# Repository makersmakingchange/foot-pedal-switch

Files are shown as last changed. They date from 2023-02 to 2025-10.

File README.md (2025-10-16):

# Foot Pedal Switch
The Foot Pedal Switch is an assistive switch with a standard 3.5 mm mono jack that can be operated with a foot.

This design is by John Park and was posted as part of an Adafruit Learning guide (https://learn.adafruit.com/diy-adaptive-game-controllers/interfacing-buttons-and-switches#foot-pedal-3015364-27).

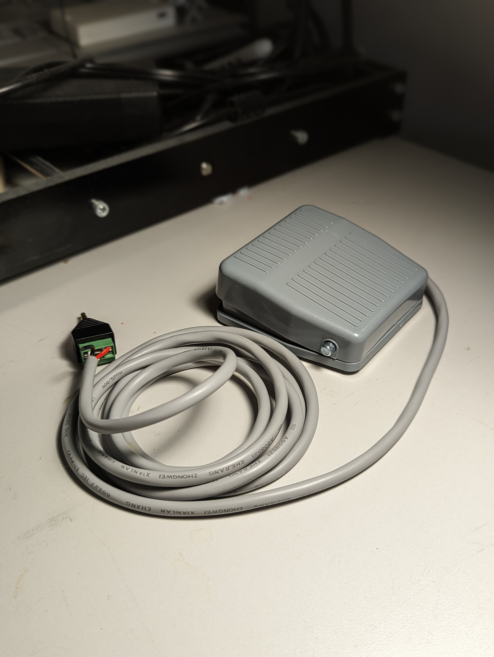
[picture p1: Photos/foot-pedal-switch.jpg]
A grey Foot Pedal Switch with an attached 3.5 mm cable sitting on a table.


## More info at
- [Makers Making Change Project Page](https://www.makersmakingchange.com/product/foot-pedal-switch/01tJR0000009Sl3YAE)

Foot Pedal Switch
### 1. Do it Yourself (DIY) or Do it Together (DIT)

This is an open-source assistive technology, so anyone is free to build it. All of the files and instructions required to build the Foot Pedal Switch are contained within this repository. Refer to the Maker Checklist below.

### 2. Request a build of this device

If you would like to obtain a Foot Pedal Switch, you may submit a build request through the [MMC Library Page](https://makersmakingchange.com/project/foot-pedal-switch/). The requestor is responsible for the cost of materials and any shipping.

### 3. How to build this device for someone else

If you have the skills and equipment to build this device, and would like to donate your time to create the switch for someone who needs it, visit the [MMC Maker Wanted](https://makersmakingchange.com/maker-wanted/) section.

## Getting Started

### 1. Read the Makers Checklist

The Makers Checklist contains a list of steps outling the process to create the device.

### 2. Order the Off-The-Shelf Components

The [Bill of Materials](/Documentation/Foot_Pedal_Switch_BOM.xlsx) lists all of the parts and components required to build the Foot Pedal Switch. The all components needs to be ordered online. 

### 3. Assemble the Foot Pedal Switch

Reference the [Assembly Guide](/Documentation/Foot_Pedal_Switch_Assembly_Guide.pdf) for the tools and steps required to build each portion.

## Files
### Documentation
| Document             | Version | Link |
|----------------------|---------|------|
| Design Rationale     | 1.2     | [Foot_Pedal_Switch_Design_Rationale](/Documentation/Foot_Pedal_Switch_Design_Rationale.pdf)     |
| Maker Checklist      | 1.2     | [Foot_Pedal_Switch_Maker_Checklist](/Documentation/Foot_Pedal_Switch_Maker_Checklist.pdf)     |
| Bill of Materials    | 1.2     | [Foot_Pedal_Switch_Bill_of_Materials](/Documentation/Foot_Pedal_Switch_BOM.xlsx)     |
| Assembly Guide       | 1.2     | [Foot_Pedal_Switch_Assembly_Guide](/Documentation/Foot_Pedal_Switch_Assembly_Guide.pdf)     |
| 3D Printing Guide    | 1.2     | [Foot_Pedal_Switch_3D_Printing_Guide](/Documentation/Foot_Pedal_Switch_3D_Printing_Guide.pdf)     |
| User Guide           | 1.2     | [Foot_Pedal_Switch_User_Guide](/Documentation/Foot_Pedal_Switch_User_Guide.pdf)    |
| Changelog            | 1.2     | [Foot_Pedal_Switch_Changelog](/Documentation/Foot_Pedal_Switch_Changelog.pdf)     |

### Design Files
 - [CAD Files](/Design_Files)

### Build Files
 - [3D Printing Files](/Build_Files/3D_Printing_Files)

## Attribution
 - Design by [John Park](https://learn.adafruit.com/diy-adaptive-game-controllers/interfacing-buttons-and-switches#foot-pedal-3015364-27)
 - Documentation by Neil Squire Society/Makers Making Change

## License
Everything needed or used to design, make, test, or prepare the Foot Pedal Switch is licensed under the [Creative Commons Attribution-NonCommercial-ShareAlike 4.0 ](https://creativecommons.org/licenses/by-nc-sa/4.0/).

Accompanying material such as instruction manuals, videos, and other copyrightable works that are useful but not necessary to design, make, test, or prepare the Foot Pedal Switch are published under a Creative Commons Attribution-ShareAlike 4.0 license https://creativecommons.org/licenses/by-sa/4.0/ (CC BY-SA 4.0).

---
<!-- ABOUT MMC START -->
## About Makers Making Change
[Makers Making Change Logo](https://www.makersmakingchange.com/)

Makers Making Change is a program of [Neil Squire](https://www.neilsquire.ca/), a Canadian non-profit that uses technology, knowledge, and passion to empower people with disabilities.

Makers Making Change leverages the capacity of community based Makers, Disability Professionals and Volunteers to develop and deliver affordable Open Source Assistive Technologies.

 - Website: [www.MakersMakingChange.com](https://www.makersmakingchange.com/)
 - GitHub: [makersmakingchange](https://github.com/makersmakingchange)
 - Bluesky: [@makersmakingchange.bsky.social](https://bsky.app/profile/makersmakingchange.bsky.social)
 - Instagram: [@makersmakingchange](https://www.instagram.com/makersmakingchange)
 - Facebook: [makersmakechange](https://www.facebook.com/makersmakechange)
 - LinkedIn: [Neil Squire Society](https://www.linkedin.com/company/neil-squire-society/)
 - Thingiverse: [makersmakingchange](https://www.thingiverse.com/makersmakingchange/about)
 - Printables: [MakersMakingChange](https://www.printables.com/@MakersMakingChange)

### Contact Us
For technical questions, to get involved, or to share your experience we encourage you to [visit our website](https://www.makersmakingchange.com/) or [contact us](https://www.makersmakingchange.com/s/contact).
<!-- ABOUT MMC END -->

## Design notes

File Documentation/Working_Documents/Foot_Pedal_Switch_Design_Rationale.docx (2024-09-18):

# Introduction

This device is a foot pedal switch that functions like a standard 3.5mm mono jack switch, but can be operated with a foot.

# Research

Name | Picture | Price | Link

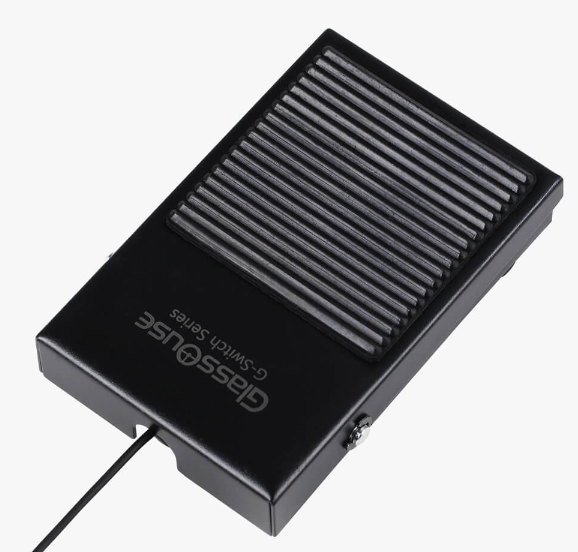
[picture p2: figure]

G-Switch GS04 | | $29.00 | Link (https://glassouse.com/product/foot-switch-glassouse-assistive-device-accessory-hands-free/)

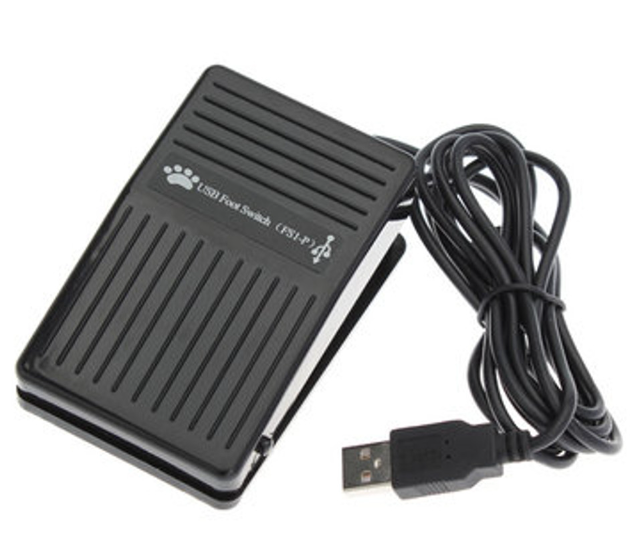
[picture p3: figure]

Single Foot Switch Computer Interface | | $41.60 | Link (https://www.adaptivetechsolutions.com/pd-single-foot-switch-computer-interface/)

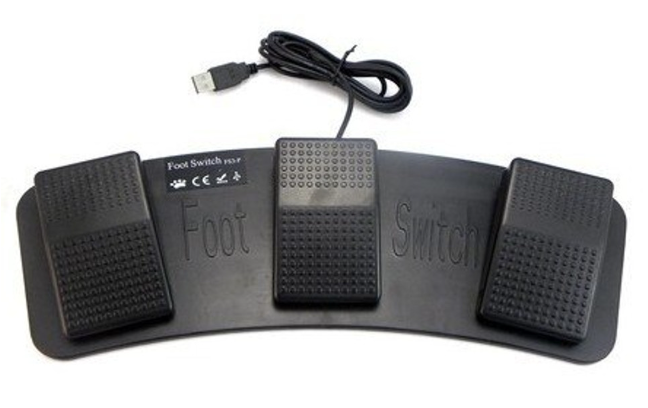
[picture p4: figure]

Three Switch Computer Controller Pedals | | $58.13 | Link (https://www.adaptivetechsolutions.com/pd-three-switch-computer-controller-foot-pedals/)

# Requirements

## Goals

G01 | Create a foot operated switch

## Functional Requirements

F01 | Activate a mono jack switch with activation of a foot pedal

## Non-functional Requirement

NF01 | Cost less than 15 dollars

## Constraints

C01 | Buildable by users with minimal experience soldering
C02 | Built using easily available components

# Testing

When the foot pedal switch was assembled, it was tested with the switch tested. It was found to have roughly a 1.5-pound activation weight and worked normally.

# Opportunities for Improvement

An enclosure could be designed to protect the wire connection between the switch and the jack.

# Metal Switch Body

It was found that for some use cases, the plastic switch body used in the original switch could shatter with heavy use, and some users wanted the cable to come out the same side as the hinge. A metal switch body was sourced on Amazon and added to the BoM and Maker Guide as an alternate design.

© 2023 by Neil Squire. This work is licensed under the CC BY SA 4.0 License: http://creativecommons.org/licenses/by-sa/4.0 Files available at https://makersmakingchange.com/project/foot-pedal-switch/ Page 1 of 1

V1.0 | February 2023 Foot Pedal Switch Design Rationale

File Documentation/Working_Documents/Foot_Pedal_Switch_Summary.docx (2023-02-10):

# Title

Foot Pedal Switch

## Subtitle

An assistive switch with a standard 3.5mm mono jack switch that is operated with a foot.

## Device Details

### Overview

This device is a foot pedal switch that functions like a standard 3.5 mm mono jack switch but can be operated with a foot.

### Usage

The switch is plugged into a 3.5 mm mono jack and can then be activated by pressing the pedal with your foot.

### Cost

~$15

### Build Instructions

This switch is assembled from commercially available components. The wires on the foot pedal switch are stripped and connected to the 3.5 mm mono jack terminal block.

#### Skills Required

- Screwdriver use
- Wire stripping

#### Time Required

- Assembly time: <5 min

#### Tools

- Wire stripper
- Screwdriver

#### Components

- 1X Foot pedal
- 1X 3.5 mm terminal jack

### Attribution

- Design by John Park (https://learn.adafruit.com/u/johnpark) on the Adafruit guide for interfacing buttons and switches (https://learn.adafruit.com/diy-adaptive-game-controllers/interfacing-buttons-and-switches)
- Documentation by Neil Squire Society/Makers Making Change

© 2023 by Neil Squire. This work is licensed under the CC BY SA 4.0 License: http://creativecommons.org/licenses/by-sa/4.0 Files available at https://makersmakingchange.com/project/foot-pedal-switch/ Page 1 of 1

V1.0 | February 2023 Foot Pedal Switch Summary

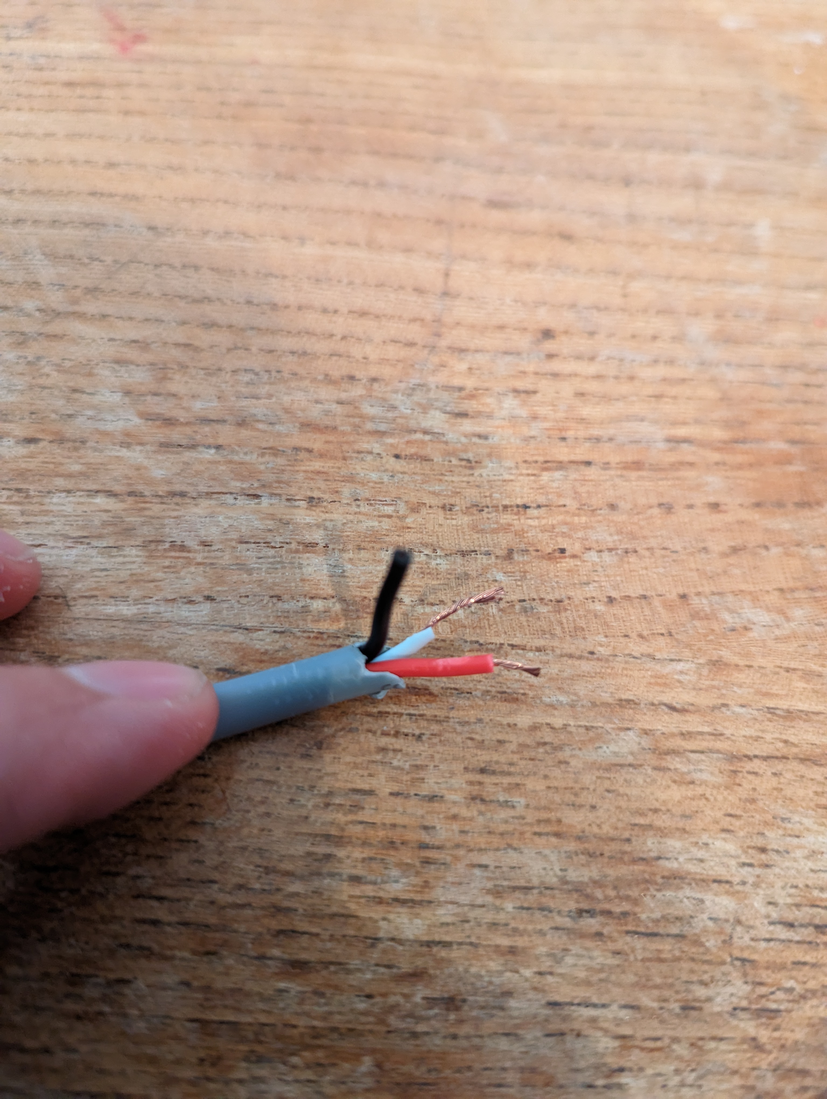
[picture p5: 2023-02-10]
Photos/Stripped wires.jpg

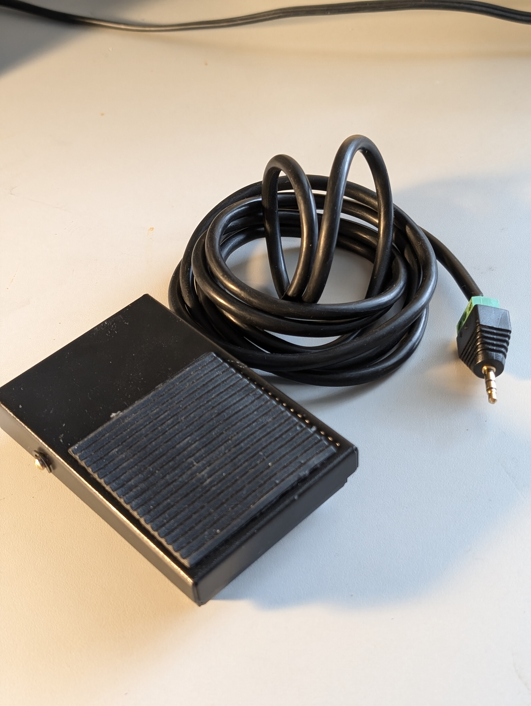
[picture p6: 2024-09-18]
Photos/Medal-Foot-Pedal-Switch.jpg

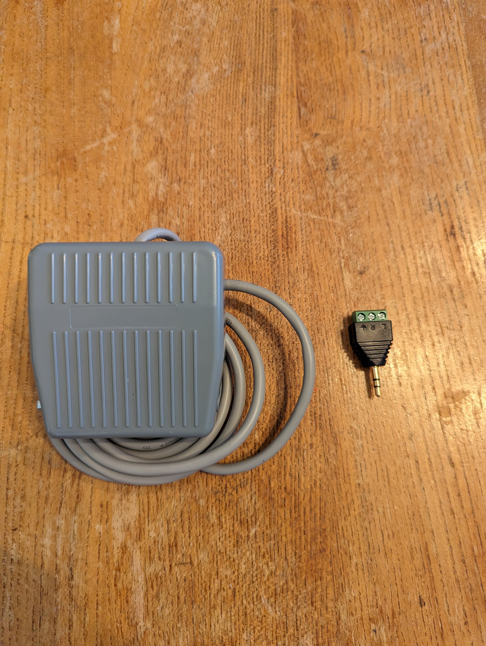
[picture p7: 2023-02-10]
Photos/Part Layout.jpg

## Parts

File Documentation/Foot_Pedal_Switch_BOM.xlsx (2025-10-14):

Foot Pedal Switch |  | Total Cost | Total Print time (hr) | Total filament (g)
Version: V1.2 | Last updated: 2024-Sept-16 | $14.84 | 1.73 | 17
Commercial Parts:
Part type (Electrical. Mechanical, Sanitization, ect) | Part Name | Quantity Needed | Pkg Quantity | Price per package | Price per Unit | Price for qty needed | Link
Electrical | Stereo Terminal Block | 1 | 1 | $3.60 | $3.60 | $3.60 | https://www.digikey.ca/en/products/detail/adafruit-industries-llc/2790/7241423
Electrical | Foot Switch | 1 | 1 | $10.81 | $10.81 | $10.81 | https://www.digikey.ca/en/products/detail/adafruit-industries-llc/423/5353597
3D Printed Parts ESTIMATED PRICING USING 1KG ROLL COST: | $25.00
Part | Description | Quantity Needed | TOTAL Mass (g) | Estimated Price | Print Time (Min) | Link
Bracket V2 | bracket to mount foot pedal to the ground | 1 | 17 | $0.43 | 104
 |  |  |  | $0.00
 |  |  |  | $0.00
 |  |  |  | $0.00
 |  |  |  | $0.00
 |  |  | Total Print Cost: | $0.43
Tools for Assembly
Wire stripper
Screwdriver
Alternatives (if there are other sources for some parts link them below)
Part and description | Link | Price
Metal Foot Pedal alternative (2-pack) | amazon.ca/gp/product/B09WN6MVVH | $23.85

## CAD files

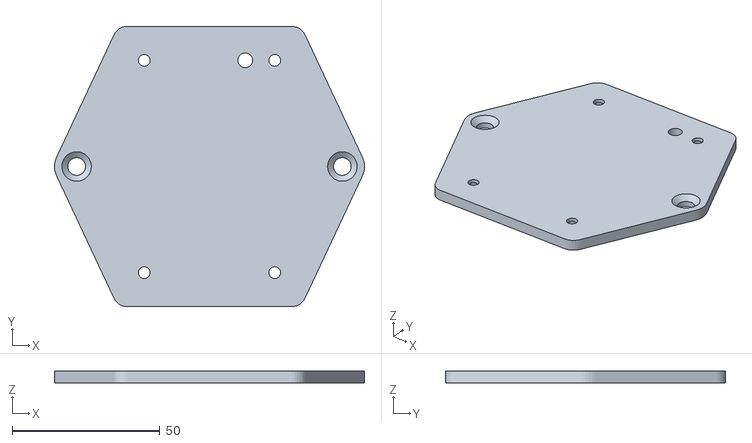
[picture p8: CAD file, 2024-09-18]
Build_Files/3D_Printing_Files/Metal Pedal Bracket.stl
105.0 x 95.0 x 4.00

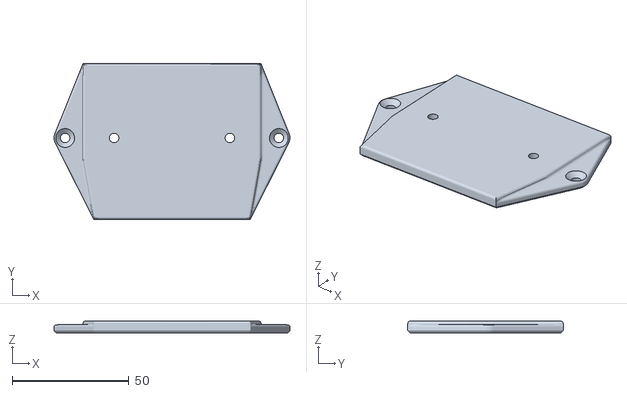
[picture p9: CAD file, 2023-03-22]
Build_Files/3D_Printing_Files/Plastic Pedal Bracket.stl
101.0 x 66.5 x 5.00

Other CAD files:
Design_Files/Metal Foot Pedal Bracket.f3d
Design_Files/Plastic Foot Pedal Bracket.f3d

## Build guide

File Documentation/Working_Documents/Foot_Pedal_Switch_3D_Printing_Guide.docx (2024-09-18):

# 3D Printing Summary

Metrics
Total Print Time (min) | 104
Total Number of Components | 2
Typical Total Mass (g) | 17
Typical Number of Print Setups | 1

# 3D Printing Settings

Print File Name | Qty | Total Print Time (hr:min) | Mass (g) | Infill (%) | Support(Y/N) | Layer Height/ Nozzle Diameter(mm) | Notes (orientation, special settings, etc.)
Plastic Pedal Bracket.stl | 1 | 1:54 | 17 | 20 | N | 0.2/0.4 | - Print in orientation given in STL
Metal Pedal Bracket.stl | 1 | 2:29 | 21 | 20 | N | 0.2/0.4 | - Print in orientation given in STL

# Customization Options

- The bracket can be printed in any colour the user would like

# Post-Processing

- Use a hobby knife or sandpaper to remove any sharp edges

© 2023 by Neil Squire. This work is licensed under the CC BY SA 4.0 License: http://creativecommons.org/licenses/by-sa/4.0 Files available at https://makersmakingchange.com/project/foot-pedal-switch/ Page 2 of 3

V1.1 | March 2023 Foot Pedal Switch 3D Printing Guide

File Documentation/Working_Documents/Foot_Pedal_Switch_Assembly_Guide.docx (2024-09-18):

# Required Components

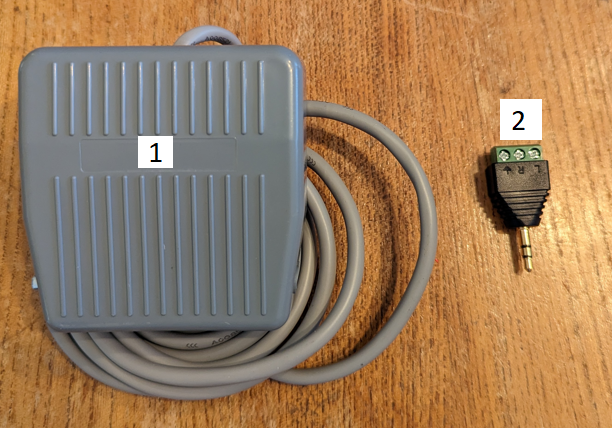
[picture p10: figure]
Both components of the foot pedal switch laid out and numbered

| BOM 1. Foot Pedal 2. Terminal Jack

# Optional Components

- Plastic Pedal Bracket
- Metal Pedal Bracket
- Metal Switch Body

# Required Tools

- Wire stripper
- Screwdriver

# Assembly Instructions

## Step 1

Strip 1 cm from the end of the pedal wire. Strip 1cm from the white and red wire as well; leave the black wire unstripped. If using the metal foot pedal, this step is the same, strip the white and red wires.

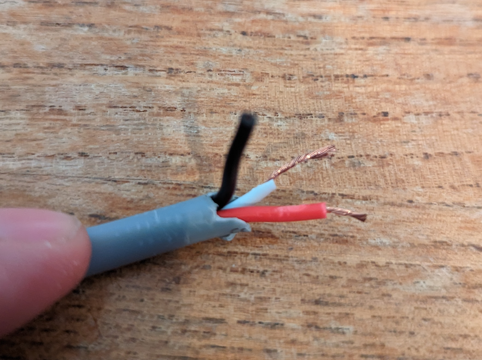
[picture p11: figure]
The grey wire casing on the pedal stripped back, with the red and white wires inside stripped as well.

## Step 2

Connect the white wire to the ground terminal on the jack, and the red wire to the L terminal on the jack. This creates a switch that is activated when the pedal is pressed. Connecting the black wire to the L terminal instead creates a switch that is always active and is deactivated when the switch is pressed. When using the metal foot pedal switch, the instructions are the same, with the white wire to the ground (right) terminal and red wire to the L (left) terminal.

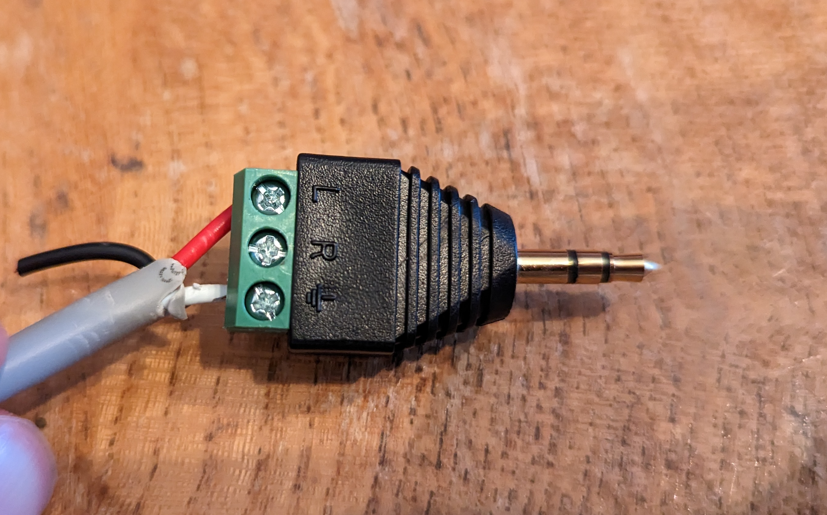
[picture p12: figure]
The terminal block attached to the red and white wires.

## Step 3 (Optional)

If using the plastic pedal bracket, remove the two screws and the four rubber feet on the bottom of the switch. The rubber feet can be removed by pulling, they are only held in place by an adhesive. Fit the bracket in place with the counterbored screw holes facing away from the switch, matching the orientation of the screws. Replace the two screws removed earlier, fastening the bracket in place. The bracket can now be screwed to a surface to hold the switch in place.

If using the metal pedal bracket, use a screwdriver to remove the feet of the pedal, and set aside the screws. Line up the bracket with the screw holes for the foot pedal and screw it into place using the screws from the feet. The bracket should only fit one way, since the screw sticking out the base only allows the bracket to fit when the hole on the bracket is aligned to the screw on the base. After the four base screws are secured, the bracket can now be screwed to a surface to hold the switch in place.

# Testing

Connect the 3.5mm jack to a switch tester or switch adapted toy and press the pedal.

## Constantly On

If the switch is constantly on, check that there are not any shorts between the wires, and that they are screwed into the correct terminal blocks in the jack. The normally open wire should be screwed into the L terminal, and the common wire should be connected to the ground terminal. Check step 2 for the correct wiring for both the plastic and metal switches.

## Constantly Off

If the switch does not turn on, check there are wires connected to the ground and L terminal on the jack. Check that the common wire is connected to the ground, and the normally open wire is connected to the L instead of both the normally closed and normally open wire both connected to the terminal. Check step 2 for the correct wiring for both the plastic and metal switches.

## Inverted

If the switch is normally on, but turns off when the switch is activated, check that the normally open wire is connected to the L terminal, instead of the normally closed wire. Check step 2 for the correct wiring for both the plastic and metal switches.

© 2023 by Neil Squire. This work is licensed under the CC BY SA 4.0 License: http://creativecommons.org/licenses/by-sa/4.0 Files available at https://makersmakingchange.com/project/foot-pedal-switch/ Page 1 of 1

V1.0 | February 2023 Foot Pedal Switch Assembly Guide

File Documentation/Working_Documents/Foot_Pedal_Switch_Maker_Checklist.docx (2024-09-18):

# Maker To Do List

- Read through the Assembly Guide to become familiar with required components, tools, supplies, and safety gear and overall assembly steps.
- Talk to User about customization options (e.g., metal switch body, brackets, any special requests, etc.)
- Order hardware components
- Gather tools, supplies, and safety equipment.
- Assemble the device
- Test device
- Print “User Quick Guide”

# Items to Give to User

- Assembled, tested device
- “User Quick Guide”

© 2023 by Neil Squire. This work is licensed under the CC BY SA 4.0 License: http://creativecommons.org/licenses/by-sa/4.0 Files available at https://makersmakingchange.com/project/foot-pedal-switch/ Page 1 of 1

V1.0 | February 2023 Foot Pedal Switch Maker Checklist

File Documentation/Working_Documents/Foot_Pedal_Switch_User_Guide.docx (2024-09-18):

## Introduction

This device is a foot pedal switch that functions like a standard 3.5mm mono jack switch but can be operated with a foot.

## Features

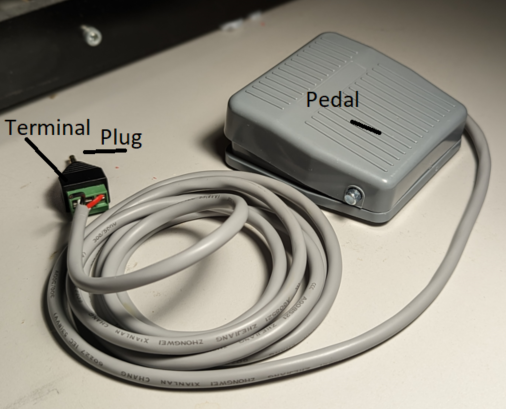
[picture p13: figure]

## Usage

To use, connect the jack to a matching 3.5 mm mono plug. The pedal can then be placed on the ground and pressed with the user’s foot to activate.

## Compatibility

The foot pedal is compatible with any device that uses a standard 3.5 mm mono jack switch. The pedal was originally designed for use with the Xbox Accessible Controller (XAC).

## Alternate Models

There is a version of the switch with a metal body that has the cable on the same side as the hinge. The metal version is listed as an alternate in the Bill of Materials and the Maker Guide.

## Specifications

The pedal has dimensions of 80 x 80 x 35 mm, and weighs 200 g. It has an activation force of 1.5 pounds.

## Cleaning

The device can be wiped clean with a damp cloth.

© 2023 by Neil Squire. This work is licensed under the CC BY SA 4.0 License: http://creativecommons.org/licenses/by-sa/4.0 Files available at https://makersmakingchange.com/project/foot-pedal-switch/ Page 2 of 3

V1.0| February 2023 Foot Pedal Switch user Quick Guide

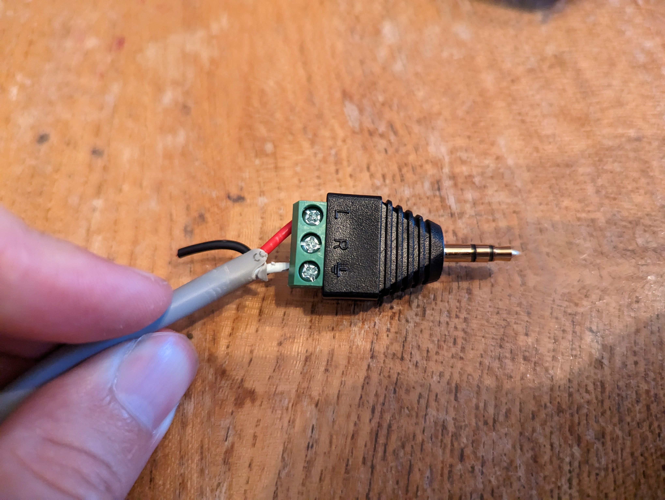
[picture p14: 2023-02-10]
Photos/Assembled terminal block.jpg

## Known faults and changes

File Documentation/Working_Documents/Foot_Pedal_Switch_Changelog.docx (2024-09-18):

# Version 1.2 | 2024/09/16

- Added an optional metal switch body that can be used in place of the plastic switch

# Version 1.1 | 2023/03/22

- Added a bracket that allows the switch to be screwed to the ground

# Version 1.0 | 2023/02/03

- Design by John Park (https://learn.adafruit.com/diy-adaptive-game-controllers/interfacing-buttons-and-switches)
- Documentation by Neil Squire Society/Makers Making Change

© 2023 by Neil Squire. This work is licensed under the CC BY SA 4.0 License: http://creativecommons.org/licenses/by-sa/4.0 Files available at https://makersmakingchange.com/project/foot-pedal-switch/ Page 1 of 1

V1.0 | February 2023 Foot Pedal Switch changelog

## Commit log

2023-02-10 Updated readme and added PDFs
    [Foot_Pedal_Switch_BOM_V1.0.xlsx]
2023-03-22 Added bracket
    added a 3D printable bracket to hold the switch in place using screws
    [Bracket V2.stl, Foot_Pedal_Switch_BOM_V1.0.xlsx, Foot_Pedal_Switch_BOM_V1.1.xlsx, Mounting Bracket V2 v5.f3d]
2024-09-18 Added metal pedal option
    Updated all files with an optional metal foot pedal body and matching mounting bracket
    [Foot_Pedal_Switch_BOM_V1.1.xlsx, Foot_Pedal_Switch_BOM_V1.2.xlsx, Metal Foot Pedal Bracket.f3d, Metal Pedal Bracket.stl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]
2025-10-14 Remove version numbering from filenames
    [Foot_Pedal_Switch_BOM.xlsx, Foot_Pedal_Switch_BOM_V1.2.xlsx]
2025-10-14 Update README.md
    Update links to match filenames without version numbers.
    Correct 3D Printing Guide typo
